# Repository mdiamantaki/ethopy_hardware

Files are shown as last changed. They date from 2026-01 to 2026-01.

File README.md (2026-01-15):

# Hardware for EthoPy

Welcome to the **Hardware for EthoPy** repository! This collection includes all hardware information required to build the setups described in EthoPy.

## What's Inside

This repo includes one folder for each behavioral system supported by EthoPy with:
- **Instructions** – step-by-step guides to build each setup with parts lists
- **Figures** – photos illustrating the construction process and final setup
- **3D designs** – ready-to-print `.stl` files

## File Structure

```
├── README.md
├── Homecage/
│   ├── README.md
│   ├── Lick_ports_assembly.md
│   ├── Speakers_assembly.md
│   └── 3d_designs/
│       ├── base.stl
│       ├── screen_holder.stl
│       └── ...
├── Open-field/
│   ├── README.md
│   └── 3d_designs/
│       └── ...
├── Air-track/
│   ├── README.md
│   └── 3d_designs/
│       └── ...
├── Spherical_Treadmill/
│   ├── README.md
│   └── 3d_designs/
│       └── ...
└── EthoPy_Controller/
    └── README.md
```

## Modifications & Contributions

Want to tweak a design? Feel free to fork the repo and customize. PRs are welcome if you want to contribute new variations or improvements!

## License

This project is licensed under the **MIT License** – see the [LICENSE](./LICENSE) file for details.

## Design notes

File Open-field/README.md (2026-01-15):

# Open-field Behavioral Setup Instructions

In this protocol, the open-field behavioral setup is used to allow freely-moving mice to perform two-alternative forced choice tasks. Below, we describe the protocol to implement an open-field behavioral setup for  a visual discrimination task.

## Hardware Parts List

### Electronics

| # | Item                               | Qty | Source                                   | Identifier                                                   | Notes                                            |
|:-:|:-:                                 |:-:  |:-:                                       |:-:                                                           |:-:                                               |

| 1 | Arduino Nano Every Board           | 1   | Arduino Store                            | ABX00028                                                     |                                                  |

| 2 | PCB Controller Board               | 1   | JLCPCB (JiaLiChuang (HongKong) Co., LTD) | [custom](../EthoPy_Controller/README.md)|  |

| 3 | 13.3" Capacitive Touch Screen LCD  | 1   | Waveshare                                | HDMI LCD (H)                                                 | Presentation of stimuli, with Toughened Glass Cover, 1920×1080 |

| 4 | HDMI Cable (2m, 4K/60Hz)           | 1   | Ugreen                                   |     ED015                                                    |Connects the screen with the PC                    |

### Other Hardware

| # | Item                                      | Qty | Source       | Identifier                                                | Notes                                                |
|:-:|:-:                                        |:-:  |:-:           |:-:                                                        |:-:                                                   |

| 1 | V-SLOT 2020 1500mm                        | 1   | Grobotronics | 27-99920208                                               | cut into 4 pieces of 31 cm length                    |

| 2 | V-SLOT 2020 250mm                         | 4   | Grobotronics | 27-99920210                                               |                                                      |

| 3 | V-SLOT 2020 500mm                         | 2   | Grobotronics | 27-99920209                                               |                                                      |

| 4 | Inside Hidden Corner Bracket 3-Way        | 4   | Grobotronics | 14-00015421                                               |                                                      |

| 5 | RatRig Cast - 90 Degree Corner Bracket    | 4   | Grobotronics | 27-22280012                                               |                                                      |

| 6 | Plexiglass Plates                         | 7   | Local vendor | —                                                         | 2 33x33cm plates, 1 30x30cm plate, 4 35x30cm plates  |

| 7 | V-Hive Enclosure Base Model               | 1   | RatRig       | HW3303GK                                                  | Insulation of light and sound                        |

| 8 | ISOLFON Foam Plate                        | —   | Muziker      | —                                                         | Sound insulator                                      |

| 9 | M4 Screws                                 | —   | M4X10        | —                                                         | 11x L10 & 16x L8                                     |

| 10| M4 T-nuts 20x20                           | 9   | —            | 14-00085144                                               |                                                      |

| 11| V-Slot Gantry Set 2020 with Three Wheels  | 2   | Grobotronics | 14-00020155                                               |                                                      |

| 12| Lickport                                  | 1   | —            | [Custom](../Homecage/Lick_ports_assembly.md) | Delivers water                                       |

| 13| LHD Series 3-Way Control Solenoid Valve   | 1   | Lee SLR      | LHDA0533415H                                              |                                                      |

### 3D Printed Parts

You will find the blueprints for the items you should 3D print [here](3d_designs).

| # | Item            | Qty | Filename                                                                                              | Notes |
|:-:|:-:              |:-:  |:-:                                                                                                    |:-:    |
| 1 | Lower Corners   | 4   | [open-field_bottom_corner.stl](3d_designs/open-field_bottom_corner.stl)    |       |
| 2 | Upper Corners   | 4   | [open-field_top_corner.stl](3d_designs/open-field_top_corner.stl)          |       |

## Step-by-step Assembly Instructions

The open-field behavioral setup is enclosed in the Rat-Rig V-Hive Enclosure Base Model ([Other Hardware list, item #7](#other7)). Assembly instructions can be found here.

### Enclosure & Sound Insulation

**Step 1**. To make the enclosure sound-proof, use sound insulation material (eg. ISOLFON foam plate, ([Other Hardware list, item #8](#other8))) to cover all sides of the enclosure, i.e. use 4 pieces with dimensions 50x50cm and 2 pieces with dimensions 50x43cm.

### Arena Construction

The interior of the enclosure consists of a plexiglass box (arena), where the mouse is placed during the experiment (base: 30x30cm, walls: 35x30 cm, ([Other Hardware list, item #6](#other6))).

**Step 2**. Glue (e.g. hot glue) each side of the arena and place 3D printed parts (3D printed parts list, items #1,2) on the upper and lower corners (Fig. 1).

<p align="center">
  
  
  
  <br>
  <em>Figure 1: Open-field arena: the arena (left), the base of the arena (center) and the arena on top of its base and inside the enclosure (right) </em>
</p>

**Step 3**. Construct the following drawer to place the arena (Fig. 1).

- `Base`: 4 V-SLOT 2020 ([Other Hardware list, item #1](#other1)) with a length of 31 cm each. Connect the rails in the shape of a square and place a plexiglass (33x33cm, Other Hardware list, item #6) in the middle. When connecting the plexiglass to the square, you need to cut its corners at around 6.1 mm.

- `Columns`: 4 V-SLOT 2020 250 mm ([Other Hardware list, item #2](#other2)). Connect them on the base.

- For the `connections` of the base and columns, use Inside Hidden Corner Brackets and M4 (8mm) screws ([Other Hardware list, item #4,9](#other4,9)).

- `Rails`: 2 V-SLOT 2020 with a length of 50 cm each ([Other Hardware list, item #3](#other3)). Place the rails on the base of the box and screw them using 4 90-Degree Corner Brackets ([Other Hardware list, item #5](#other5)). To screw the brackets on the V-SLOTS, use M4 screws (10mm, ([Other Hardware list, item #9](#other9))) and M4 20x20 Tee Nuts (Other Hardware list, item #10).

- `Sliding`: Screw 2 V-Slot Gantry Sets 2020 with Three Wheels ([Other Hardware list, item #11](#other11)) on each side of the base with M4 (8mm, ([Other Hardware list, item #9](#other9))) screws and M4 20x20 Tee Nuts ([Other Hardware list, item #10](#other10)). Attach each V-Slot Gantry Set to the rails.

### Screen

**Step 4**. Place a screen ([Electronics list, item #3](#electro3)) on the one side of the box between the 2 V-slots (Fig. 2).

**Step 5**. Connect the cable for power (included in the 13.3inch Capacitive Touch Screen LCD, ([Electronics list, item #3](#electro3))) and the HDMI ([Electronics list, item #4](#electro4)) (Fig. 1).

<p align="center">
  
  
  <br>
  <em>Figure 2: Screen: front side of the screen (left) and back side of the screen and connections (right)</em>
</p>

### Arduino Board

**Step 6**. Follow instructions for [EthoPy Controller Board](../EthoPy_Controller/README.md)

### Lickport

**Step 7**. Follow instructions [here](../Homecage/Lick_ports_assembly.md) to make the lickport ([Other Hardware list, item #12](#other12)).

**Step 8**. Connect the lickport to the arduino board and a solenoid valve ([Other Hardware list, item #13](#other13)) in a pressurized tubing network (STAR methods, liquid delivery).

### Extra Parts

To record the experiment you will aslo need red LED lights and a camera capable of recording fps>30 and a fov>80&deg; (We used Arducam 2.3MP AR0234 Color Global Shutter USB 3.0)

### PC Requirements
For the Open-field setup in the EthoPy project, in addition to the standard installation, you will need to enable real-time pose estimation by installing `DeepLabCut-Live`, which provides a lightweight, low-latency inference pipeline for online tracking. To achieve frame rates greater than 30 FPS, we strongly recommend using a system running Ubuntu paired with a powerful NVIDIA GPU (minimum 8GB VRAM), as this ensures compatibility with TensorFlow and allows for GPU-accelerated inference. CPU-only systems or unsupported GPUs (e.g., Intel or AMD) will not meet the real-time demands.

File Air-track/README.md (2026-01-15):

# Air-track setup

In this paradigm, head-fixed mice perform a visual two-alternative forced choice task. This setup can be adapted to accommodate more sensory modalities by using appropriate equipment.

<p align="center">
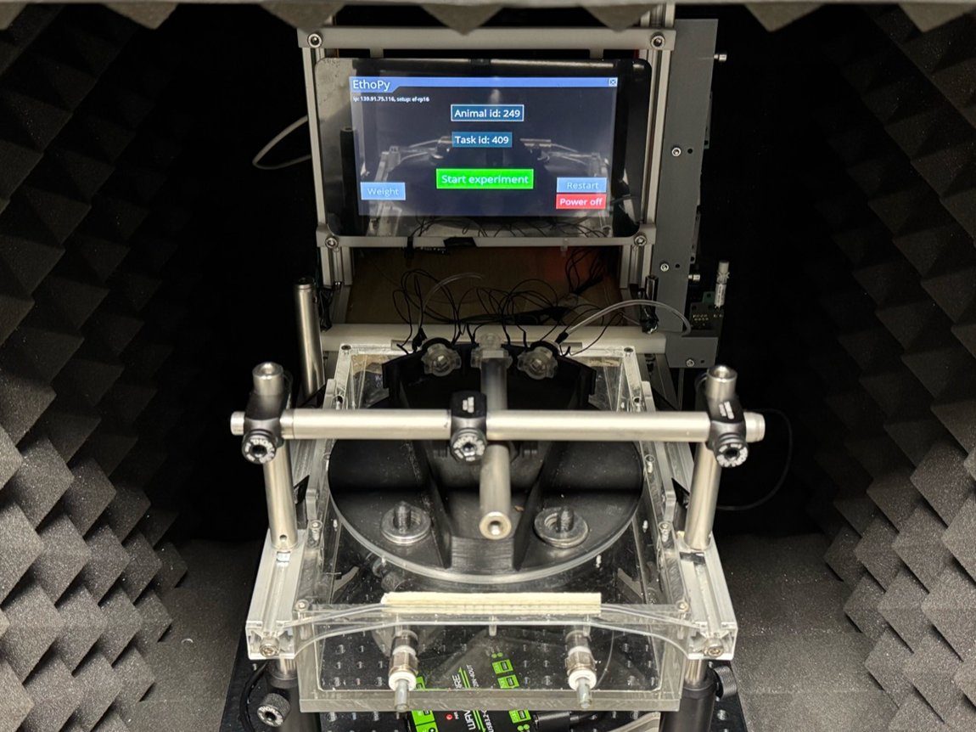
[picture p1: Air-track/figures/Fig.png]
  
</p>

## Hardware Parts List

### Electronics

| # | Item | Qty | Source | Identifier | Notes |
|:-:|:-:|:-:|:-:|:-:|:-:|

| 1 | Bpod port interface board | 3 | Sanworks | 1008 | Controlling the behavior ports |

| 2 | solenoid valves | 2 | LEE | LHDA0533415H | |

| 3 | Infrared Emitter 880nm Circular Right Angle 2-Pin Side Looker | 3 | Honeywell | SEP8736-002 | For the behavior ports |

| 4 | Phototransistor IR Chip Silicon 880nm 2-Pin Side Looker | 3 | Honeywell | SDP8436-002 | For the behavior ports |

| 5 | Ethernet cable | 3 | Bel | BC-5UK005F | |

| 6 | Cable 0.05 mm², Ø 0.8mm | 1 | TRU_ | 1567774 | |

### Other Hardware

| # | Item | Qty | Source | Identifier | Notes |
|:-:|:-:|:-:|:-:|:-:|:-:|

| 1 | Plexiglas air-table | 1 | Provided by Mostafa A. Nashaat, Larkum Lab, Larkum Lab, Charite, Berlin | | |

| 2 | PLA platform | 1 | Provided by Mostafa A. Nashaat, Larkum Lab, Charite, Berlin | | |

| 3 | Behavior port | 3 | | | |

| 4 | Crimp For Dupont Female | 15 | Ninigi | NDR-T | |

| 5 | Tygon S3™ E-3603 Tubing (water) Ø Inner 2.38mm, Ø outer 3.97mm | 4 pieces | Optubus | TY2,38ST3,97 | |

| 6 | Tygon S3™ E-3603 Tubing (water) Ø Inner 0.79mm, Ø outer 2.38mm | 2 pieces | Optubus | TY0,79ST2,38 | |

| 7 | V-Hive Enclosure Base Model | 1 | RatRig | HW3303GK | |

| 8 | Sound insulator ISOLFON foam plate | 4 pieces 50x50cm and 2 pieces 50x43cm | Mega Acoustic | 244317 (PA-PMP5-DG-5050) | for sound and light insulation |

| 9 | Heat shrink set | | GROBOTRONICS | 05-00017098 | |

### 3D printed parts

You will find the blueprints for the items you should 3D print [here](3d_designs).

| # | Item | Qty | Filename |
|:-:|:-:|:-:|:-:|
| 1 | screen holders | 2 | [screen_holder.stl](3d_designs/screen_holder.stl) |

## Step-by-step Assembly instructions

You will find the blueprints for the items you should 3D print [here](3d_designs).

> **Info:** The  air-table ([see Other Hardware, part #1](#hardware1)) and platform ([see Other Hardware, part #2](#hardware2)) of the air-track were developed by Dr. Mostafa A. Nashat and assembly (https://doi.org/10.1152/jn.00088.2016, https://doi.org/10.1101/2024.08.22.608577).

**Step 1**. Set up the [Raspberry Pi Behavioral Setup](../Homecage/README.md) following steps 1-7, modifying Raspberry Pi Behavioral Setup Step 5 to connect only the valves ([see Electronics, part #2](#electro2)) to the EthoPy Controller Board.

**Step 2**. Mount the Raspberry Pi Behavioral Setup on the screen holders ([see 3D printed parts, part #1](#printed1)) in front of the air-table (Fig. 1).

<p align="center">
  
  
  <br>
  <em>Figure 1: The RP behavioral setup, mounted on the aluminum rails of the air-table using the screen holders.</em>
</p>

**Step 3**. Assembling of a behavior port ([see Other Hardware, part #3](#hardware3)). Mounting of the infrared emitter ([see Electronics, part #3](#electro3)) and phototransistor ([see Electronics, part #4](#electro4)) to the port was performed following the instructions provided [here](https://sanworks.github.io/Bpod_Wiki/assembly/mouse-behavior-port-assembly/). Each platform included three behavior ports.

> **Note:** For our experiments, we did not include LED light in the behavior ports.

**Step 4**. Set up three Bpod port interface boards ([see Electronics, part #1](#electro1)) as per instructions provided [here](https://sanworks.github.io/Bpod_Wiki/assembly/port-breakout-board-assembly/). Place the Bpod port Interface Boards close to the Air-track and the Raspberry Pi Behavioral Setup for convenience.

**Step  5**. For each port, connect the infrared emitter and phototransistor with the Bpod port interface board.

> **Note:** To reduce the tension caused to the platform from these connections, prefer using wires with a cross-section of 0.05 mm² and an outer diameter of 0.8 mm ([see Electronics, part #6](#electro6)).

**Step 6**. Connecting the Bpod port interface boards to the Raspberry Pi Behavioral Setup. As the connections with the Bpod port interface board are through an Ethernet cable, you will need 3 Ethernet cables, one per port ([see Electronics, part #5](#electro5)).

**Step 7**. Remove the insulation from the edge of the Ethernet wires. Place 13 female terminals ([see Other Hardware, part #4](#hardware4)) at the end of each wire and cover the exposed terminal with insulation (e.g., heat shrink tube, [see Other Hardware, part #9](#hardware9)). In the following steps, the identification of the Ethernet cable wires is shown in (Fig. 2).

<p align="center">
  
  <br>
  <em>Figure 2: Ethernet cable wire number ids.</em>
</p>

> **Note:** You will use the wires 1 (signal of the sensor), 4 (power of the emitter), 5 (ground).

**Step 8**.  The wires from the Ethernet cables are connected to the Raspberry Pi Behavioral Setup (see GPIO connections as set in [EthoPy documentation](https://ef-lab.github.io/ethopy_package/local_conf/?h=channel#4-schema-names-optional)) as follows:

- Connect `wire 1` (signal) of each Ethernet cable to the <ins>respective GPIO pin</ins> for the proximity input of each port.
- Connect `wire 4` (power) of each Ethernet cable to a <ins>5V power pin</ins>.
- Connect `wire 5` (ground) of each Ethernet cable to a <ins>ground pin</ins>.

> **Note:**  Power cables and grounds should be short-circuited together to connect to one pin of the Raspberry Pi.

**Step 9**. Driving of the valves for ports 1 and 2 using the [EthoPy Controller Board](../EthoPy_Controller/README.md).

**Step 10**. Adjust the reward tubes ([see Other Hardware, part #5](#hardware5), [part #6](#hardware6)) to the behavioral port and connect the valves. Bridge the valves and connect to the water supply (Fig. 3).

<p align="center">
  
  <br>
  <em>Figure 3: Solenoid valve with the positions of the tubes</em>
</p>

**Step 11**. If sound/light insulation is needed, the Air-track behavioral system can be enclosed in the [Rat-Rig V-Hive Enclosure Base Model](https://ratrig.dozuki.com/Guide/01.+V-Hive+Enclosure+Base+Model/183?lang=en) ([see Other Hardware, part #7](#hardware7)). For further sound and light insulation, related insulation material (e.g. ISOLFON foam plate, see ([see Other Hardware, part #8](#hardware8))) can be used to cover the sides of the enclosure.

**Step 12**. The behavioral system should be placed in a room with air supply, needed for the floating of the platform on the air-table and the water delivery.

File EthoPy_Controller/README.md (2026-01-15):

# EthoPy Controller Board and Arduino

Arduino is a microcontroller that converts the analog signal from the lick and proximity ports to digital, and a Controller Board ensures the communication between the Arduino and Raspberry Pi.

<p align="center">
  
</p>

## Parts List

### Electronics

| # | Item                                      | Qty  | Source                       | Identifier              | Notes |
|:-:|:-:                                        |:-:   |:-:                           |:-:                      |:-:    |

| 1 | 40-pin Stackable Female Extra Tall Header | 1    | Grobotronics                 |                         |       |

| 2 | Arduino Nano Every                        | 1    | Arduino Store                |                         |       |

| 3 | 1x2 Female Pin Header Right Angle         | 2    | Grobotronics                 | 05-00011907             |       |

| 4 | 1x3 Female Pin Header Right Angle         | 3    | Grobotronics                 | 05-00011907             |       |

| 5 | 1x2 Male Pin Header                       | 5    | Grobotronics                 | 19-00011916             |       |

| 6 | 1x15 Female Pin Header                    | 2    | Grobotronics                 | 19-00011915             |       |

| 7 | 1x15 Male Pin Header                      | 2    | Included in Arduino kit      | —                       |       |

| 8 | Metal Film Resistor 100 Ω, 1/4W, 1%       | 4    | YAGEO                        | MFR25SFTF52-100R        |       |

| 9 | Metal Film Resistor 2.2 kΩ, 1/2W, 1%      | 3    | YAGEO                        | MFR25SFTF52-2K2         |       |

| 10 | Metal Film Resistor 1 kΩ, 1/2W, 1%       | 3    | YAGEO                        | CFR-25JB-1K0            |       |

| 11 | Metal Film Resistor 10 kΩ, 1/4W, 1%      | 3    | YAGEO                        | CFR25SJT-52-10K         |       |

| 12 | BC547B Transistor                        | 2    | onsemi / Fairchild           | BC547B                  |       |

| 13 | Aluminium Electrolytic Capacitor         | 1    | Rubycon                      | 35ZLR220MEFC8X11.5      |       |

| 14 | Tactile Push Button Switch (6×6×6)       | 2    | Same Sky                     | TS02-66-70-BK-160-SCR-D |       |

| 15 | Tactile Push Button Switch (6×6×9)       | 1    | —                            |                         | —     |

| 16 | Diode Rectifier                          | 2    | Vishay General Semiconductor | 1N4005-E3/73            |       |

| 17 | Printed Circuit Board (PCB)              | 1    | Custom                       | —                       |       |

<p align="center">
  
  <br>
  <em>Figure 1: EthoPy Controller Board and Arduino parts</em>
</p>

> **Note:** You will also need: a soldering iron, a wire cutter

## Step-by-Step Assembly Instructions

**Step 1**. Print the PCB board of the schematic (Fig. 2). PCB and gerber files for JLPCB will be available in a future update.

<p align="center">
  
</p>

**Step 2**. Solder the 1x15 female pin headers on each side of the Arduino Nano Every board (Fig. 3).

<p align="center">
  
  
</p>

**Step 3**. Solder each resistor into its designated position on the PCB according to its resistance value (Fig. 4).

<p align="center">
  
</p>

**Step 4**. Solder the five 1x2 male pins headers into the corresponding ports on the PCB (Fig. 5).

<p align="center">
  
</p>

**Step 5**. Solder the transistors onto their correct positions on the board (Fig. 6).

<p align="center">
  
</p>

**Step 6**. Solder the diodes in the same way (Fig. 7).

<p align="center">
  
</p>

**Step 7**. Solder the tactile push button switch in the appropriate position on the board (Fig. 8).

<p align="center">
  
</p>

**Step 8**. Solder the capacitor, ensuring the longer positive lead goes into the right hole (Fig. 9).

<p align="center">
  
</p>

**Step 9**. Solder the right-angle female pin headers - two on the left side (1x2) for valves and three on the bottom (1x3) for ports and centerport (Fig. 10).

<p align="center">
  
</p>

**Step 10**. Solder the two 1x15 female pin headers for the Arduino board (Fig. 11).

<p align="center">
  
</p>

**Step 11**. Mount the Arduino board onto the previously mentioned female pin headers (Fig. 12).

<p align="center">
  
  
</p>

**Step 12**. Solder the 40-pin extra-tall stackable female header to connect the PCB to the Raspberry Pi board (Fig. 13).

<p align="center">
  
</p>

**Step 13**. Set up the Arduino using the code provided [here](EthoPy_Controller_code.ino).

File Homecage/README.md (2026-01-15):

# Raspberry Pi Behavioral Setup
A key component of multiple Ethopy behavioral systems is the [Raspberry Pi](https://www.raspberrypi.com/), a small, affordable, single-board computer. It includes ports for HDMI, USB, Ethernet, audio, camera interface (CSI), display interface (DSI), and General Purpose Input/Output (GPIO) pins. It primarily runs on a Linux-based OS called Raspberry Pi OS, and also supports other operating systems. Below, we analytically describe the steps to implement a Raspberry Pi-based behavioral setup.

<p align="center">
  
</p>

## Hardware Parts List

### Electronics

| # | Item                                          | Qty     | Source              | Identifier            | Notes                                                                                     |
|:-:|:-:                                            |:-:      |:-:                  |:-:                    |:-:                                                                                        |

| 1 | Raspberry Pi 4 Model B/4GB                    | 1       | Raspberry Pi             |SC0192-3|                                                                                           |

| 2 | Official Raspberry Pi 7 Touch Screen Display  | 1       | Raspberry Pi              |  2473872         |                                                                                           |

| 3 | Premium High Speed microSD Card               | 1       |  Integral  | INMSDH32G-100/70V30              |                                                                                           |

| 4 | EthoPy Controller Board                       | 1       | [Custom](../EthoPy_Controller/README.md)              |                       |                                                                                           |

| 5 | Lick Ports                                    | 2 or 3  | [Custom](Lick_ports_assembly.md)              |                       | 2 to detect licks and deliver water, 1 can be used as a proximity indicator (center port) |

| 6 | Beam Photoelectric Sensor                     | 1       | HAITRONIC               | HR0172          |Can be used as a proximity indicator (center port)                                         |

| 7 | Solenoid valves                               | 2       | LEE SLR         | LHDA0533415H               |                                                                                           |

| 8 | Ultrasound Speakers 40kHz                     | 2       | PUI Audio      | UT-1640K-TT-2-R    |For auditory experiments. See: [Speakers_assembly](Speakers_assembly.md)                                                                    |

### Other Hardware

| # | Item                                | Qty | Source      | Identifier    | Notes       |
|:-:|:-:                                  |:-:  |:-:          |:-:            |:-:          |

| 1 | M3 screws                           | 6   | Grobotronics  | M3X12/D7985  |             |

| 2 | Raspberry Pi 4 Heatsink (40x30x5mm) | 1   | Grobotronics  | 49-00012076  |             |

### 3D Printed Parts
You will find the blueprints for the items you should 3D print [here](3d_designs).
| # | Item                          | Qty | Filename                                                                                            | Notes                           |
|:-:|:-:                            |:-:  |:-:                                                                                                  |:-:                              |
| 1 | Base                          | 1   | [base.stl](3d_designs/base.stl)                                            | Includes the lick port holders  |
| 2 | Screen holder                 | 2   | [screen_holder.stl](3d_designs/screen_holder.stl)                          |                                 |
| 3 | Center port holder            | 1   | [center_port.stl](3d_designs/center_port.stl)                              |                                 |
| 4 | Center port & speaker holder  | 1   | [center_port_with_speakers.stl](3d_designs/center_port_with_speakers.stl)  | Includes speaker holders        |
| 5 | Pins                          | 1   | [pin.stl](3d_designs/pin.stl)                                              | For mounting the center port holder |

<p align="center">
  
  
  <br>
  <em>Figure 1: RP setup (top: 3D printed parts of the RP's base, bottom: assembled RP base).</em>
</p>

## Step-by-step Assembly Instructions

**Step 1**. Install the [operating system of the RPi](https://www.raspberrypi.com/documentation/computers/getting-started.html#installing-the-operating-system). In our experiments, we have used the [Bullseye Raspberry Pi OS](https://www.raspberrypi.com/news/raspberry-pi-os-debian-bullseye/).

**Step 2**. Mount the Raspberry Pi to the Raspberry Pi Touch Display and connect the Flat Flexible Cable and the power of the Touch Display to the Raspberry Pi [instructions](https://www.raspberrypi.com/documentation/accessories/display.html).

**Step 3**. Connect the Ethopy Controller Board to the RPi.

**Step 4**. Add a heatsink ([Other Hardware parts list, item #2](#other2)) on the back of the RP to avoid excessive warming.

**Step 5**. Plug in the side and the center ([lick](Lick_ports_assembly.md) or interruptor) ports, and the valves to the EthoPy Controller Board, to the positions indicated on the board.

**Step 6**. Connect the valves to the water supply. Each LEE valve ([Electronics parts list, item #7](#electro7)) has 3 pipe-edges (1) to be connected to the lick port tube, (2) to be connected with the water supply tube, and (3) to be connected with the other valve through a tube and 2 pins to be connected to the board (Fig. 2, left).

In the RP setup, the upper valve corresponds to the left lick port, and the bottom valve corresponds to the right lick port (Fig. 2, right).

<p align="center">
  
  
  <br>
  <em>Figure 2: Connections of the solenoid valve (left: positions of the tubes, right: placement of the valves on the RP board).</em>
</p>

**Step 7**. Connect to the RPi and run a test task.

- ssh username@ip_address 

> For more information, visit their: [Rasberry Pi: Remote access](https://www.raspberrypi.com/documentation/computers/remote-access.html)

- Follow the instructions on how to [install/run EthoPy](https://ef-lab.github.io/ethopy_package/installation.html)

> **Note (Optional):** Rename the RP and set a static IP address.

> **Tip:** When using multiple RPs, it is best to use unique names that follow a consistent structure and assign static IP addresses to each RP to facilitate identification and management. To do this, connect to the RP and change its default name following the [instructions](https://ef-lab.github.io/ethopy_package/raspberry_pi). It is recommended to use a fixed prefix followed by an incremental number for each RP added.

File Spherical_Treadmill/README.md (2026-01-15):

# Spherical Treadmill Behavioral Setup

The Spherical Treadmill (ball) behavioral setup is used for head-fixed mice performing sensory navigation tasks (e.g., olfactory, visual, multimodal). Below, we describe the protocol to construct an odor-based virtual reality setup.

<p align="center">
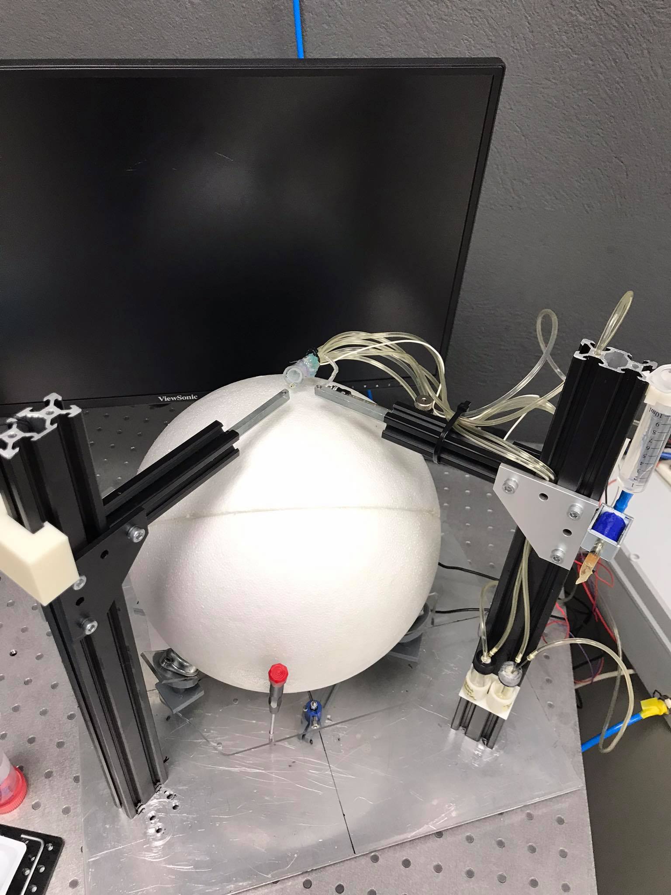
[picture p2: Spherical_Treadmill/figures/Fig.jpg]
  
</p>

## Hardware Parts List

### Electronics

| # | Item                      | Qty  | Source          | Identifier   |  Notes                                 |
|:-:|:-:                        |:-:   |:-:              |:-:           |:-:                                     |

| 1 | solenoid valves           | 5    | fspumb.cn       | 0526T        | 4 for odorants, 1 for water delivery   |

| 2 |MOSFET board               | 5    | OEM             | FR120N       | To control the solenoid valves         |

| 3 | Capacitive sensor board   | 1    | Sparkfun        | AT42QT1011   | for lick detection                     |

| 4 | laser mouse               | 2    | DELL            | MS3220       | ball sensors                           |

### Other Hardware

| # | Item                      | Qty  | Source          | Identifier   |  Notes                                 |
|:-:|:-:                        |:-:   |:-:              |:-:           |:-:                                     |

| 1 | ball bearings             | 3    | DFRobot         | FIT0007      |                                        |

| 2 | plastic box               | 1    | Kradex          | Z74HJ        | 30 x 20 x 10cm                         |

### 3D Printed Parts

You will find the blueprints for the items you should 3D print [here](3d_designs).

| # | Item                  | Qty | Filename                                                                        | Notes             |
|:-:|:-:                    |:-:  |:-:                                                                              |:-:                |

| 1 | mouse post            | 2   | [mouse_post.stl](3d_designs/mouse_post.stl)                 |                   |

| 2 | ball bearing holder   | 3   | [ball_bearing_holder.stl](3d_designs/ball-bearing-post.stl) |                   |

| 3 | 5-way tube connector  | 1   | [tube_connector.stl](3d_designs/tube_connector.stl)         |                   |

## Step-by-Step Assembly Instructions

Following instructions apply for any virtual reality system that uses a styrofoam ball on 3 ball bearings (similar to Fig. 4d of the EthoPy paper) <!--Add hyperlink-->, 4 odours to define an olfactory virtual environment, and a mouthpiece to deliver the odors but also the reward.

**Step 1**. Set up the [Raspberry Pi Behavioral Setup](../Homecage/README.md) following steps 1-5, the difference is that in this setup you need 5 valves ([Electronics parts list, item #1](#electro1)), for reward and 4 for odour delivery.

**Step 2**. A `Styrofoam ball` is supported by three (3) metallic ball bearings ([Other Hardware parts list, item #1](#other1)) allowing smooth navigation for prolonged periods. The bearings are supported by custom 3D-printed posts ([3D-printed parts, part #2](#printer2)) at a 45° angle, so the ball is stable while the subject is performing the task.

<p align="center">
  
  <br>
  <em>Figure 1: Animated depiction of the experimental set-up. Mouse is head-fixed onto a styrofoam ball, with a mouthpiece securing the odor and water delivery.</em>
</p>

**Step 3**. The PCB boards of the laser mice ([Electronics parts list, item #4](#electro4)) are used as sensors to encode the ball movement. Laser mice holders ([3D-printed parts, part #1](#printer1)) are used to place the laser mice in an optimal position at 90⁰ degrees from each other, very close to the bearings, and at an incline of 55°, to eliminate the distance variation between the ball and the sensor that could lead to imprecise tracking information. Insert the PCB board of each laser mouse and ensure they have 2-3 mm distance from the surface of the ball (Fig. 2).

<p align="center">
  
  <br>
  <em>Figure 2: Schematic of the locations of the ball bearing holders (grey) and the laser mice (red).</em>
</p>

> **Note:** Details about the how EthoPy computes the distances covered by the animal are in [`vr_ball_readme.md`](https://github.com/ef-lab/ethopy_plugins/blob/main/spherical_treadmill/behaviors/vr_ball_readme.md)

**Step 4**. The odor and water delivery system requires constant air supply and 5 solenoid valves. The air supply is connected to a 5-way manifold ([3D-printed parts, part #3](#printer3)) with the 4 valves that open and close when a pulse is sent from the RP through the MOSFET ([Electronics parts list, item #2](#electro2)). Upon pulse delivery the valves open for the specified duration and the air travels through the odor bottle to the mouthpiece. Similarly for the water supply, water is delivered to the lick port inside the mouthpiece upon correct response. 

> **Note:** Odors are released depending on the animal's virtual location and are calculated in [`EthoPy Ball`](https://github.com/ef-lab/ethopy_plugins/blob/main/spherical_treadmill/stimuli/vr_odors_readme.md) 

<p align="center">
  
  <br>
  <em>Figure 3: Animated depiction of the assembly of the stimuli that arrive at the mouthpiece odors (left) and water (right). </em>
</p>

### Electrical Connections

- `Valves’ control circuit`: To control the valves, we use a MOSFET board ([Electronics parts list, item #2](#electro2)) and connect the power and ground of the valve to the board, placing the power at position 2a and the ground at position 2b shown in [Fig. 4](#fig4). Then, to connect it with the Raspberry Pi, we select the pin of the RP we have programmed to trigger the valve and a ground pin and connect the other end to the PWR and GND pins respectively placed at the top part of the board (position 3, (Fig. 4)). Lastly, to turn on the board we need to insert 2 cables at position 1, one for the power and one for the ground of the power supply. In this last step, it is advised to make a 6-way cable assembly, both for the power and the ground, 5 of them going to each MOSFET board, and one connecting the power supply. This assembly can be placed in a plastic box ([Other Hardware parts list, item #2](#other2)).

<p align="center">
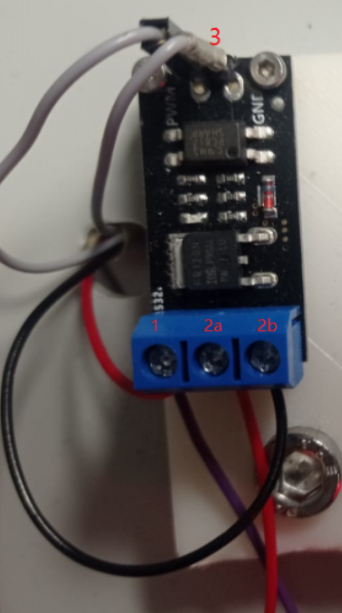
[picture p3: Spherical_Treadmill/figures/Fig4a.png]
  
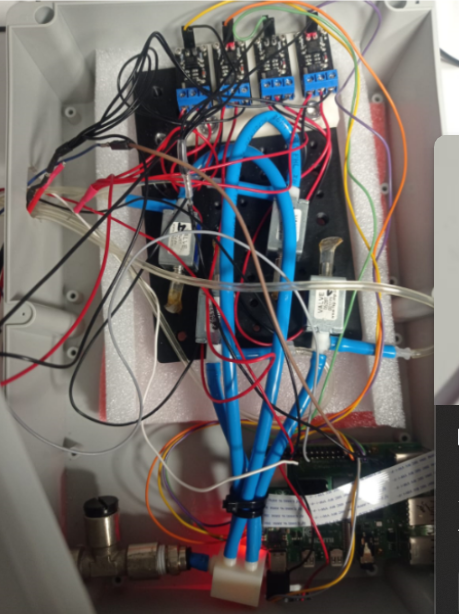
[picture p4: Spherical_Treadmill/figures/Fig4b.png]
  
  <br>
  <em>Figure 4: MOSFET boards for controlling the valves for the odorants </em>
</p>

- `Lick detector circuit`: The Capacitive sensor board ([Electronics parts list, item #3](#electro3)) consists of five pins: GND for ground, OUT for signal, VDD for power supply (1.8V - 5V), LED and PAD (Fig. 5). In this case, only four of the pins are required (GND, OUT, VDD, and PAD). To connect the sensor for the lick detection it is important to solder a trimmed and polished 18G needle to the wire that will connect with the PAD pin. 

<p align="center">
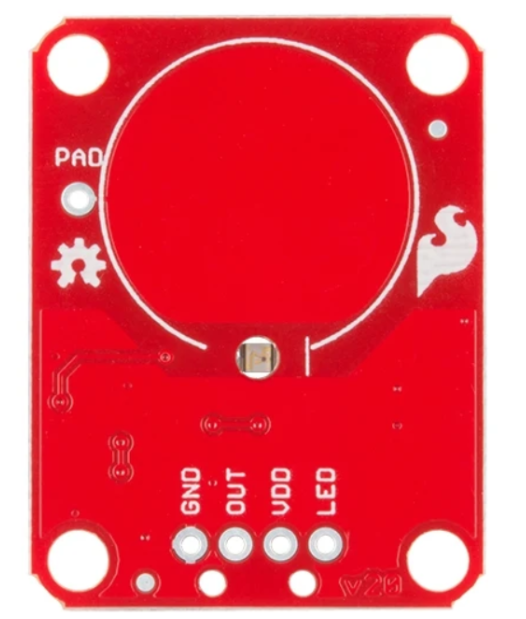
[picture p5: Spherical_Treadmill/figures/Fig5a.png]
  
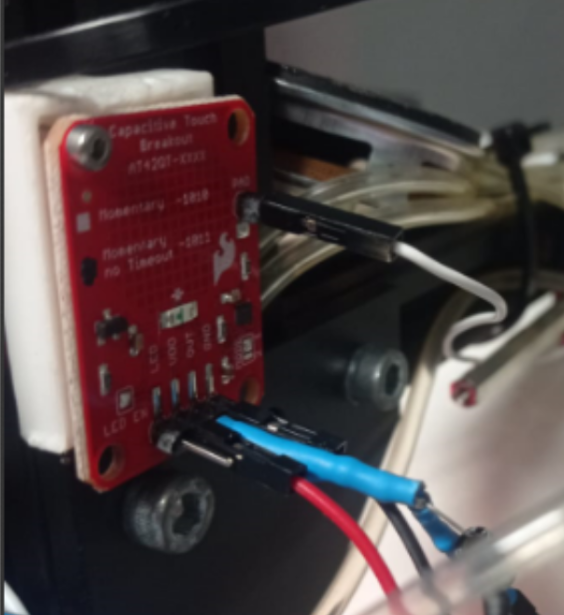
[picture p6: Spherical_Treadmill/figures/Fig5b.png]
  
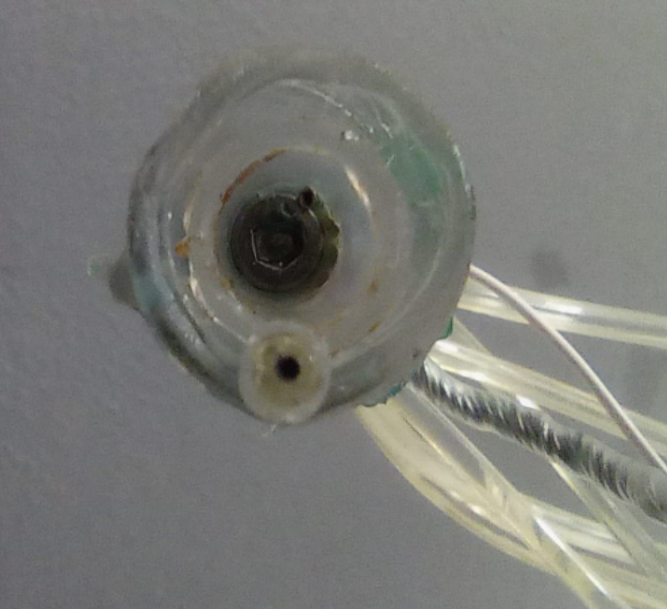
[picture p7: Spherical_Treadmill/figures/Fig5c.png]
  
  <br>
  <em>Figure 5: Capacitive Touch Breakout board and Mouthpiece</em>
</p>

- `Laser mice`: Connect the laser mice to the two USB ports of the RP (each USB port will be assigned later in EthoPy code (Interfaces/Ball.py) to determine which laser mouse is responsible for decoding which axes)

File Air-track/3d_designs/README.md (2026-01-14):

# 3D Designs for EthoPy Hardware

This folder contains 3D-printable `.stl` files for components used in the adapted Air-track to be used with EthoPy.

## Included Models

- `screen_holder.stl` – Stand for screen placement

All models are designed for ease of printing and assembly, with minimal support requirements.

## Recommended Print Settings

> We use a Zortrax M200 Plus with the Z-ULTRAT material and the default settings and support. However, other FDM printers and ABS, PLA, PETG material should also work. Adjust for your printer as needed.

## Notes

- Make sure to orient parts flat on the print bed to avoid unnecessary supports.
- All parts can be printed in the current orientation

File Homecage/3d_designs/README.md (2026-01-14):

# 3D Designs for EthoPy Hardware

This folder contains 3D-printable `.stl` files for components used in the EthoPy Homecage setup.

## Included Models

- `base.stl` – Main mounting base
- `center_port.stl` – Center nose-poke port
- `center_port_with_speakers.stl` – Center nose-poke port for the auditory tasks
- `screen_holder.stl` – Stand for screen placement
- `pin.stl` – For mounting the center port holder

All models are designed for ease of printing and assembly, with minimal support requirements.

## Recommended Print Settings

> We use a Zortrax M200 Plus with the Z-ULTRAT material and the default settings and support. However, other FDM printers and ABS, PLA, PETG material should also work. Adjust for your printer as needed.

## Notes

- Make sure to orient parts flat on the print bed to avoid unnecessary supports.
- All parts can be printed in the current orientation

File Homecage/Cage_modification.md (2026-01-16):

# Cage Modification for the Raspberry Pi–Based Behavioral Setup

This document describes the procedure for drilling holes in standard mouse cages
(**1264C EUROSTANDARD TYPE II**) to accommodate proximity/lick ports (and speakers, if required) for the Homecage System.

Hole positions are defined using fixed spatial distances to ensure reproducibility and proper alignment with the Raspberry Pi–based behavioral setup (RP).

---

## 🧭 Overview of the Procedure

1. Define hole positions using fixed distances
2. Prepare the cage
3. Align the cage with the RP and screen
4. Drill pilot holes
5. Enlarge holes to final diameter
6. Drill the central lick port
7. Smooth all interior surfaces
8. Verify alignment and finish

---

## 📐 Hole Geometry and Distances

Before drilling, review the required spatial arrangement of lick ports and speakers and confirm alignment with the 3D-printed base and ports.

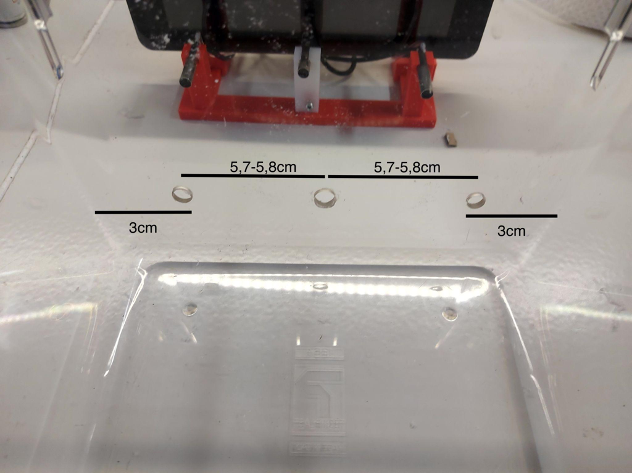
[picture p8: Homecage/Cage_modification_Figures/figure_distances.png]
Distances between ports


⚠️ **Important:**  
All hole positions should be determined using these distances. Do not rely solely on visual alignment.

---

## 🛠️ Required Tools

- Permanent marker
- Drill
- HSS drill bit (2.5 mm)
- Step drill (metric scale)
- Caliper
- Multi-tool with sanding tip  
  *or* sanding paper and hot air gun
- Safety equipment (gloves, eye protection)

---

## 📋 Procedure

### Step 1 – Cage Preparation
Clean the cage thoroughly. Make sure that the cage has no permanent marks or visible scratches.

📝 **Note:**  
If needed for identification purposes, label the cage with the corresponding **RP_id** at this stage.

---

### Step 2 – Initial Alignment
To confirm the exact locations, place the cage in front of an RP and confirm that the cage is centered in front of the screen.

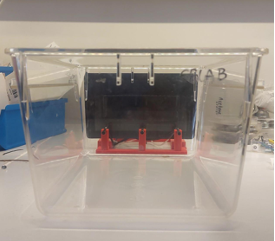
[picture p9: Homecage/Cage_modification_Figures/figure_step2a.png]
Cage aligned with RP and screen

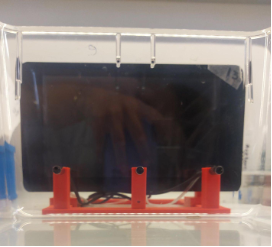
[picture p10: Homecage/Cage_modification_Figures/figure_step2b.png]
Cage aligned with RP and screen


---

### Step 3 – Marking Hole Positions
Using the distances shown above, mark the positions of the two lateral lick ports on the **interior surface** of the cage.

- Mark one dot at the center of each port location.
- Use a caliper or ruler for accuracy.

---

### Step 4 – Drilling Pilot Holes
Use a small drill at the beginning (**HSS 2.5 mm**) and drill a hole exactly on each mark.

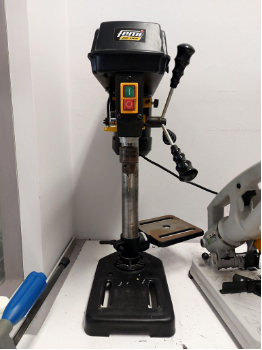
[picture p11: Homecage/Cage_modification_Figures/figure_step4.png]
Drilling pilot holes


---

### Step 5 – Verification of Alignment
Place the cage in front of the RP and make sure the holes match the center of each lick port.

⚠️ **ATTENTION:**  
Perform this check every time the holes are modified to ensure correct alignment.

---

### Step 6 – Enlarging the Holes
Use the step drill to broaden the holes.

⚠️ **ATTENTION:**  
- Use the scale markings to control the final diameter.
- Ensure the scale is in **millimeters**, not inches.
- Verify diameter using a **caliper**.

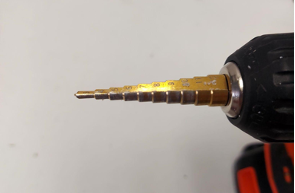
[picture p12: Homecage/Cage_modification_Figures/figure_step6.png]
Enlarging holes with step drill


---

### Step 7 – Final Hole Diameters
- Final diameter of each lick port hole: **~7.5 mm**

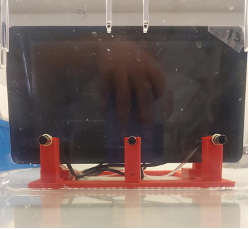
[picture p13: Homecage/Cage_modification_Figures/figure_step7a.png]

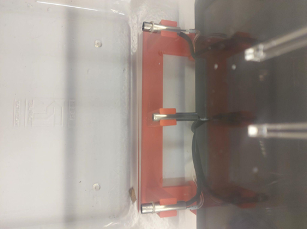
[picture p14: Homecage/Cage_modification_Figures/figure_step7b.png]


If speakers are part of the setup:
- Final diameter of each speaker hole: **~8.5 mm**

---

### Step 8 – Central Lick Port
After completing the lateral holes, place the cage in front of the RP and mark the center of the **central lick port** using the same distance-based method.

Repeat **Steps 4–7** for the central lick port.

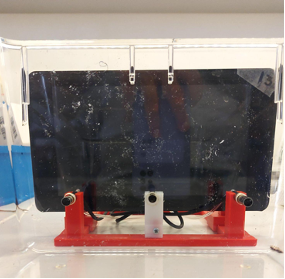
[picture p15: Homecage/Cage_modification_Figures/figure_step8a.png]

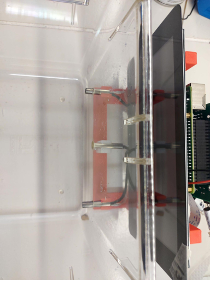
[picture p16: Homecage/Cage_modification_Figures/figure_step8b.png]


---

### Step 9 – Smoothing the Holes
Make the interior of all holes smooth to prevent irritation to the mouse.

Options:
- Use a **multi-tool with a small sanding tip**, or
- Use sanding paper followed by a **hot air gun (scale 1)** for a few seconds.

⚠️ **Be careful not to melt the plastic cage.**

Check smoothness gently with your finger.

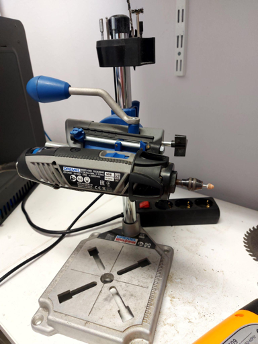
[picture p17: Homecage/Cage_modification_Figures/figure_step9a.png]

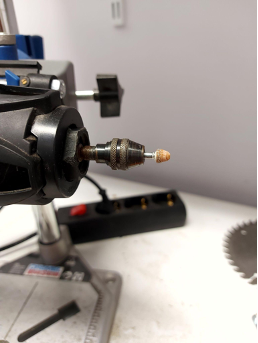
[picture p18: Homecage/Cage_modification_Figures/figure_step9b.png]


---

## ✅ Final Verification

- Confirm that all holes align correctly with the lick ports and speakers.
- Confirm that all hole edges are smooth.
- Confirm that hole diameters match specifications.

The cage is now ready for assembly.

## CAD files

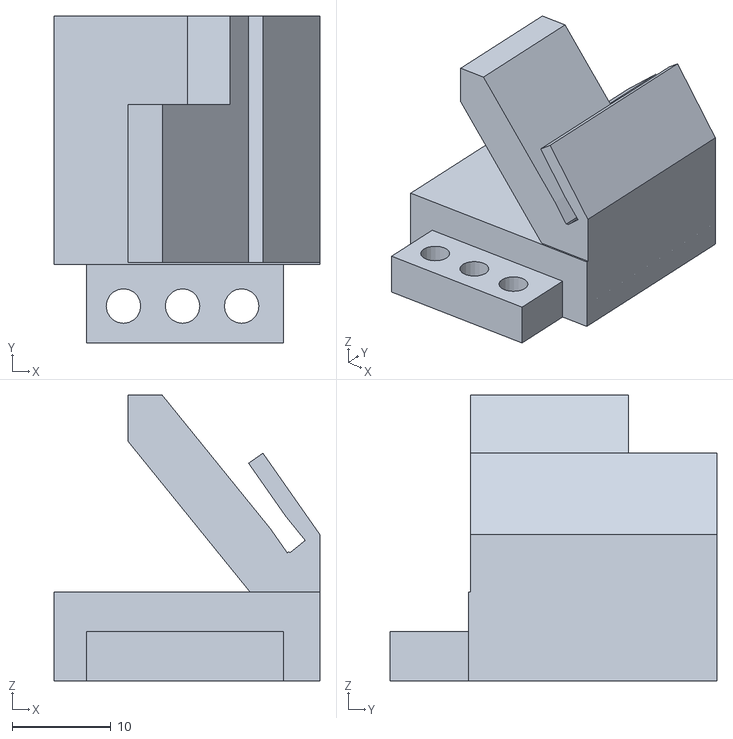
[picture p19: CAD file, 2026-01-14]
Spherical_Treadmill/3d_designs/mouse_post.stl
27.0 x 33.2 x 29.0

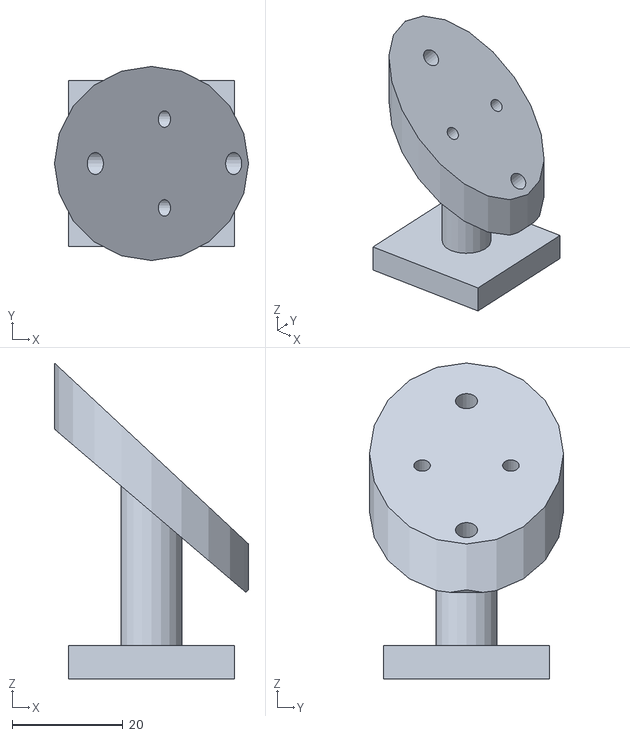
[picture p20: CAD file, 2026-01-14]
Spherical_Treadmill/3d_designs/ball-bearing-post.stl
35.0 x 35.0 x 57.0

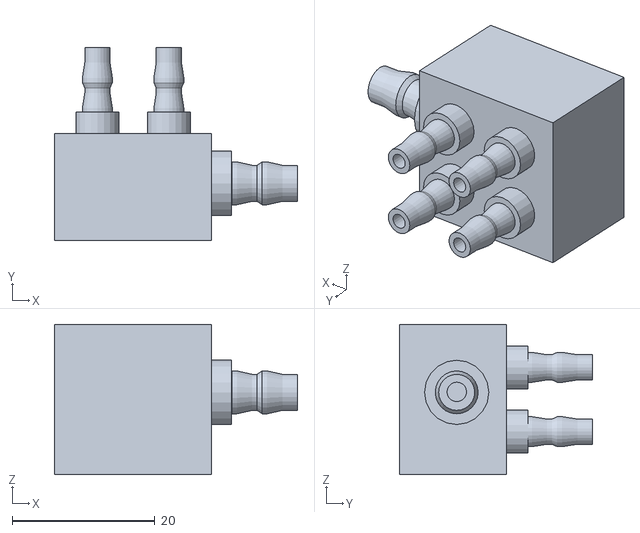
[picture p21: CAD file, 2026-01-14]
Spherical_Treadmill/3d_designs/tube_connector.stl
34.0 x 27.0 x 21.0

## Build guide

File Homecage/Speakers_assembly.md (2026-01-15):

# Speakers' Setup
Speakers are used to provide auditory cues during behavioral experiments. They can be embedded within experimental setups to deliver sound stimuli. Below are the step-by-step instructions for setting up the speakers.

<p align="center">
  
</p>

## Hardware Parts List

### Electronics
| # | Item                           | Qty  | Source            | Identifier      | Notes                            |
|:-:|:-:                             |:-:   |:-:                |:-:              |:-:                               |

| 1 | Ultrasound Speakers 40kHz      | 2    | PUI Audio         | UT-1640K-TT-2-R | Transmitter                      |

| 2 | Speaker (Receiver)             | 1    | —                 | —               |                                  |

| 3 | Jumper wire (female-to-female) | 2    | GROBOTRONICS      | 05-00011907     |                                  |

| 4 | Heat shrink set                | 6    | Cyg, Grobotronics | 05-00017098     | Two 12cm and four 20cm Jumper wire |

### 3D Printed Parts
You will find the blueprints for the item you should 3D print [here](3d_designs/center_port_with_speakers.stl).

## Step-by-Step Assembly Instructions

**Step 1**. Select four long female-to-female jumper wires and connect one end of each to the pins of the speaker (Fig. 1). Repeat this step twice.

<p align="center">
  
  <br>
  <em>Figure 1: Speaker connected with female-to-female jumper wires</em>
</p>

**Step 2**. Remove the square female heads from the other ends of the wires.

**Step 3**. Solder the ends of two jumper wire (one from each speaker) together along with one small female-to-female jumper wire (after removing its square female head) (Fig. 2).

<p align="center">
  
  <br>
  <em>Figure 2: Soldering ends of two jumper wires</em>
</p>

**Step 4**. Cut a piece of heat shrink tube long enough to cover the exposed wires (Fig. 3).

<p align="center">
  
  <br>
  <em>Figure 3: Coverd part with heat shrink tube</em>
</p>

**Step 5**. Use the oscilloscope and connect one end (measuring clip) to one wire of the speaker and the grounding clip to the other wire (Fig. 5).

<p align="center">
  
  <br>
  <em>Figure 5: .....</em>
</p>

**Step 6**. Connect your speakers to your Raspberry Pi Pinout. First, go to the `EthoPy/Interfaces/RPPorts.py` and look at the `class RPPorts(Interface)`. Here, you see which channel corresponds to the RP GPIO pins based on what you want to connect. So for **sound** is channel `GPIO 13` (Fig. 6) that has been set in the local_conf.json, for more details check [here](https://ef-lab.github.io/ethopy_package/local_conf/#3-logging-settings-optional).

<p align="center">
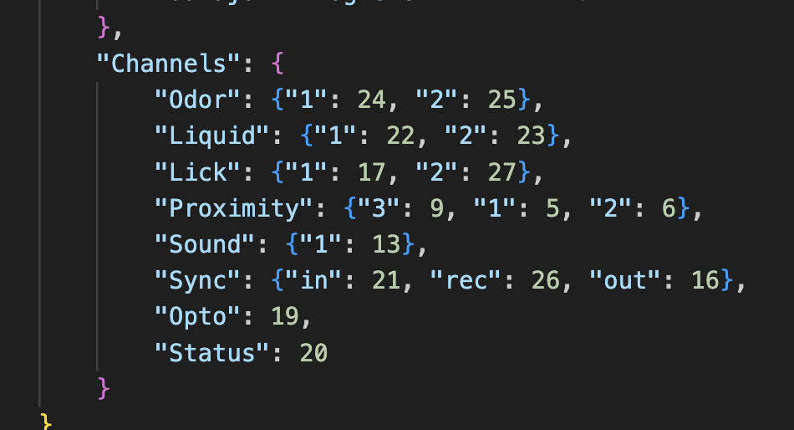
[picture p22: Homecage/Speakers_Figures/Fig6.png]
  
  <br>
  <em>Figure 6: Hardware mapping of behavioral sensor ports to GPIO pins</em>
</p>

Connect one wire of your speaker to `GPIO13` and the other wire to `ground`(Fig. 7).

<p align="center">
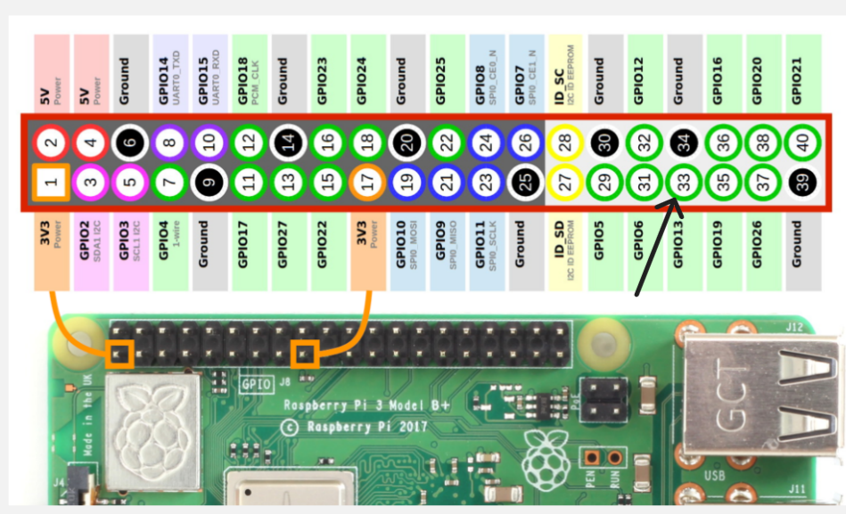
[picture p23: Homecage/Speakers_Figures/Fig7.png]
  
  <br>
  <em>Figure 7: Rasberry Pi's GPIO pins</em>
</p>

**Step 7**. Open your RP and run a task with auditory stimuli.

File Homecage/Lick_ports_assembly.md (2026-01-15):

# Lick ports

Lick Ports are used both for lick detection and reward delivery. Regarding the former, lick ports include a LED and a photo sensor positioned in parallel. Close vicinity of an object (e.g. the tongue of a mouse) reflects the infrared light and activates the photosensor. This signal is connected to the control circuit board that links them with the computational node (Raspberry Pi or PC). Regarding the latter, a tube for water delivery for correct responses is coupled to a computerized valve that controls the liquid delivery that can deliver liquid volumes with 1μL resolution. The water is channeled through a liquid delivery device when the correct electrical signal is transmitted from the port to the electric control panel leading to the opening of the respective valve. Both the LED and photo sensor wires and the reward tubes are enclosed and glued in a metal cylinder at their end point in order to prevent possible damages that could be caused by chewing or other mice activities.

<div align="center">
  <figure id="fig">
    
  </figure>
</div>

## Hardware Parts List

### Electronics

| # | Item                                                          | Qty       | Source                   | Identifier         | Notes                                                       |
|:-:|:-:                                                            |:-:        |:-:                       |:-:                 |:-:                                                          |

| 1 | Shielded cable                                                | 25–28 cm  | Belden                   | 1804A              | To protect the signal from electrical noise and interference |

| 2 | Optical switch (Phototransistor)                              | 1         | Onsemi                   | QRE1113            |                                                             |

| 3 | Wirewound Resistor - Through hole EP 2W (SS, 330Ω, 5%)        | 1         | TE Connectivity          | EP2WSS330RJ        | To control the current flow                                 |

| 4 | Metal Film Resistor - Through hole 0.6W 50ppm CECC (47kΩ, 1%) | 1         | Vishay / Beyschlag       | MBB0207VC4702FCT00 | To control the signal output voltage                        |

### Other Hardware

| # | Item                                                          | Qty       | Source             | Identifier  | Notes                                                                                                                         |
|:-:|:-:                                                            |:-:        |:-:                 |:-:          |:-:                                                                                                                            |

| 1 | Heat shrink set                                               | 6         | Cyg, Grobotronics  | 05-00017098 | 4x1/16'' - for the individual wires 1x3/16'' - for the sensor's side 1x1/4'' or 1x3/8'' - for the phototransistor's side     |

| 2 | Welded Stainless Steel Tubing 6 mm OD, 0.25 mm Wall Thickness | 3–4 cm    | McMaster-Carr      | 50415K25    |                                                                                                                               |

| 3 | Unolok Disposable Needle (18G)                                | 1         | HMD                | 100445      | For reward delivery                                                                                                           |

| 4 | Male Pin Header (1×40, 2.54mm)                                | 3 pins    | Grobotronics       | 19-00011916 |                                                                                                                               |

| 5 | Soldering Wire Cynel 100g 0.5mm - Lead Free                   | —         | Grobotronics       | 05-00605630 |                                                                                                                               |

| 6 | Bison 5 minutes epoxy glue                                    | —         | Bison              | 6305448     |                                                                                                                               |

## Step-by-Step Assembly Instructions

### Connecting the cable to the sensor

**Step 1**. Cut the ends of the phototransistor ([Electronics parts list, item #2](#electro2)). pin connectors to shorten them to a few millimeters.

**Step 2**. Strip the outer insulation from the cable ([Electronics parts list, item #1](#electro1)). to expose the individual wires, then strip each wire to reveal the inner conductors.

**Step 3**. Slide a small piece of heat shrink tube (1/16’’) onto each wire ([Other Hardware parts list, item #1](#other1)). Make sure it covers both the pins of the sensor and the exposed wire (do not heat the heat shrink tube yet, just move it to the base of each wire).

**Step 4**. Each of the 4 pins of the phototransistor corresponds to a specific wire. The pin positions start from the trimmed edge of the rectangle (Pin 1), and the rest follow in an anticlockwise direction ([Fig. 1](#fig1)).
- `Pin 1`: anode of the LED (connects to the power supply)
- `Pin 2`: cathode of the LED (connects to the ground)
- `Pin 3`: collector of the sensor (current flow after light reflection)
- `Pin 4`: emitter of the sensor (connects to the signal output)

<div align="center">
<figure id="fig1">
  
  
  <figcaption><b>Figure 1</b>: <i>Positions of the phototransistor’s pins and their corresponding wires.</i></figcaption>
</figure>
</div>

**Step 5**. Use the soldering station to connect the pins vertically to their corresponding wires as described below ([Fig. 2](#fig2)).

**Step 6**. Use a hot air gun to heat the heat shrink tubes you have added to each wire to cover the wire and the phototransistor’s pins.

<div align="center">
<figure id="fig2">
  
  <figcaption><b>Figure 2</b>: <i>Heat shrink tubes covering the exposed wires and the phototransistor’s pins.</i></figcaption>
</figure>
</div>

**Step 7**. Cut a piece of heat shrink tube (3/16’’) long enough to cover the exposed cable and the pins of the phototransistor, and pass it down the cable. Αpply the epoxy glue ([Other Hardware parts list, item #6](#other6)) to the exposed section of the cable and cover it up to the edge. Cover the exposed cable with the heat shrink tube and use the hot air gun to heat it. Ensure that the phototransistor’s pins and the wires are well covered.
Note: As the hot air gun shrinks the tube, ensure that the epoxy glue will not cover the phototransistor.

<div align="center">
<figure id="fig3">
  
  <figcaption><b>Figure 3</b>: <i>Heat shrink tube covering the phototransistor side of the lick port.</i></figcaption>
</figure>
</div>

**Step 8**. Cut a steel cylinder ([Other Hardware parts list, item #2](#other2)). long enough to cover the heat shrink tube that covers the exposed wires ([Fig. 4](#fig4)). Carefully smooth both edges of the cylinder with sandpaper to ensure the mouse is not injured while licking it.

**Step 9**. Cut the pointy edge of the 18G needle ([Other Hardware parts list, item #3](#other3)). and smooth it with sandpaper. Remove the plastic hub from the needle. Ensure that the needle is long enough to extend beyond the bottom end of the steel cylinder so that it can be properly connected to the water tube ([Fig. 4](#fig4)).

> **Note:** The needle is required only if you will use the lick port for reward delivery.

<div align="center">
<figure id="fig4">
  
  <figcaption><b>Figure 4</b>: <i>Indicative lengths of the steel cylinder and the needle relative to the lick port.</i></figcaption>
</figure>
</div>

**Step 10**. Pass the phototransistor cable and the needle through the steel cylinder. Apply epoxy glue around the heat shrink tube insulation of the phototransistor ([Fig. 5](#fig5)) and the needle, ensuring that the phototransistor’s and the needle’s tops are not covered with glue. Pull the cable and the needle so that they are on the same level and a few millimeters below the top of the steel cylinder to prevent possible damage. Fill all the empty spaces between the phototransistor and the cylinder with epoxy glue.

<div align="center">
<figure id="fig5">
  
  <figcaption><b>Figure 5</b>: <i>Phototransistor end of the lick port.</i></figcaption>
</figure>
</div>

### Connecting the cable to the resistors

You will need two resistors:
- `330Ω`: The anode of the LED is connected to the power through the 330Ω resistor to control the current flowing through the LED.
- `47kΩ`: The resistor is placed between the emitter of the phototransistor and the ground to help define the signal output voltage.

**Step 11**. Shorten the wire connected to the anode and expose the conductor. Cut both ends of the 330Ω resistor ([Electronics parts list, item #3](#electro3)) and use soldering to connect the 330Ω resistor to the wires connected to the anode and the collector. Solder the resistor horizontally across the cable, connecting the distal pin to the collector wire and the proximal pin to the anode wire ([Fig. 6](#fig6)).

<div align="center">
<figure id="fig6">
  
  <figcaption><b>Figure 6</b>: <i>Connections of the 330Ω resistor.</i></figcaption>
</figure>
</div>

**Step 12**. Shorten the wire connected to the emitter and expose the conductor. Βend one of the pins of the 47KΩ resistor ([Electronics parts list, item #4](#electro4)). Use soldering to connect the cathode wire to the straight pin and the emitter wire to the other pin ([Fig. 7](#fig7)).

<div align="center">
<figure id="fig7">
  
  <figcaption><b>Figure 7</b>: <i>Connections of the 47kΩ resistor.</i></figcaption>
</figure>
</div>

**Step 13**. Use a male pin header ([Other Hardware parts list, item #4](#other4)) with 3 pins and connect it to the cable ([Fig. 8](#fig8)). Mark the tip that is connected to the bent pin of the 47kΩ resistor so you can distinguish it (it corresponds to the signal).

<div align="center">
<figure id="fig8">
  
  <figcaption><b>Figure 8</b>: <i>Connections of the signal cable (<b>P</b>: power, <b>G</b>: ground, <b>S</b>: signal).</i></figcaption>
</figure>
</div>

**Step 14**. Cover the exposed cable and the proximal part of the male pin header with heat shrink tube (1/4’’ or 3/8’’), and heat it with the hot air gun.

### Testing the lick ports

**Step 15**. Provide a DC power supply (∼3.5V). Connect the positive terminal to the power input and the negative terminal to the ground in the pins shown in ([Fig. 8](#fig8)).

**Step 16**. Use an oscilloscope and connect it to the signal cable ([Fig. 8](#fig8)).

**Step 17**. Use your finger to simulate the lick of a mouse and observe the activation of the phototransistor ([Fig. 9](#fig9)).

<div align="center">
<figure id="fig9">
  
  
  <figcaption><b>Figure 9</b>: <i>Sensor voltage output (left: connections of the power supply and the oscilloscope, right: activation of the phototransistor).</i></figcaption>
</figure>
</div>

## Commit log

2026-01-14 Restructure documentation and fix broken links
    - Rename all main instruction files to README.md for automatic GitHub display
    - Fix broken internal links by using relative paths instead of ethopy_hardware/ prefix
    - Remove all emojis from section headers and documentation
    - Standardize directory naming: rename 3d_design/ to 3d_designs/
    - Fix typos: assemply → assembly, gerder → gerber
    - Rename assembly files: Lick_ports_assemply.md → Lick_ports_assembly.md, Speakers_assemply.md → Speakers_assembly.md
    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
    [ball-bearing-post.stl, mouse_post.stl, tube_connector.stl]
2026-01-14 Clean up assembly documentation and fix table formatting
    - Clean up Lick_ports_assembly.md and Speakers_assembly.md
    - Remove all emojis from section headers
    - Fix typo: assemply → Assembly
    - Remove HTML comments
    - Standardize table spacing and formatting
    - Fix duplicate item number in Speakers (two #3s)
    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
2026-01-16 add drilling holes instructions in Homecage
